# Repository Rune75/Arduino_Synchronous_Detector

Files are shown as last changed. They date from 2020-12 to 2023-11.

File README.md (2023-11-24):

# Arduino Synchronous Detector

This code demostrates a low frequency lockin amplifier or synchronous ligth detector inplementation using only a Arduino board and 2 additional modules: 
  1. The OPT101 amplified vissible light photodiode 
  2. A laser pointer 
  
The syncronous detector components are all realised in software 
using the Atmega328p builtin ADC as frontend and one GPIO for driving the laserdiode.

## Whys and hows
The idea behind a synchronous detector or lockin amplifier is best described trough an example. So lets asume we want to detect a moving target at some  distance. To be able to do this one could for example shine some ligth on the target and look for changes in the reflected light. If setting up this experiment with a light source and a photosensor we will soon discover that the reflected light variation we are trying to measure is not distingusable from variations in the ambient light level as shown in the top figure below. If we instead modulate our signal source with some frequency and lock our detector to the same frequency and phase we have what is called a synchronous detector. 

As shown below the synchronous demodulation process cancels out ambient noise and we are left with the signal of interest only.

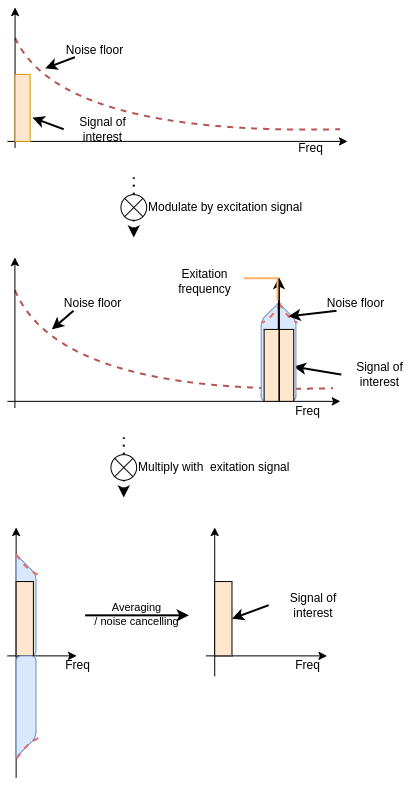
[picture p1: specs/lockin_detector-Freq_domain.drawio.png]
Frequncy domain


Thie noise cancelation part is a bit hard to grasp in the frequncy domain, but if we instead consider that the modulated source is realy just swithing on an off the light source at a constant frequency, and thus on the receiver side the same bacground noise will be present in both halfperiodes of the signal, both when the ligth source is on and when it is off. The demodulator is just a multiplicator that multiplies the signal with a square waveform with amplitude +1 to -1. at the same frequencuy and phase as the source modulation. The +- multiplication basicaly flips the sign on the noise in each halfperiode so the noise average over time from the demodulator is close to zero. This process is shown in the following figure.

### Basic principle
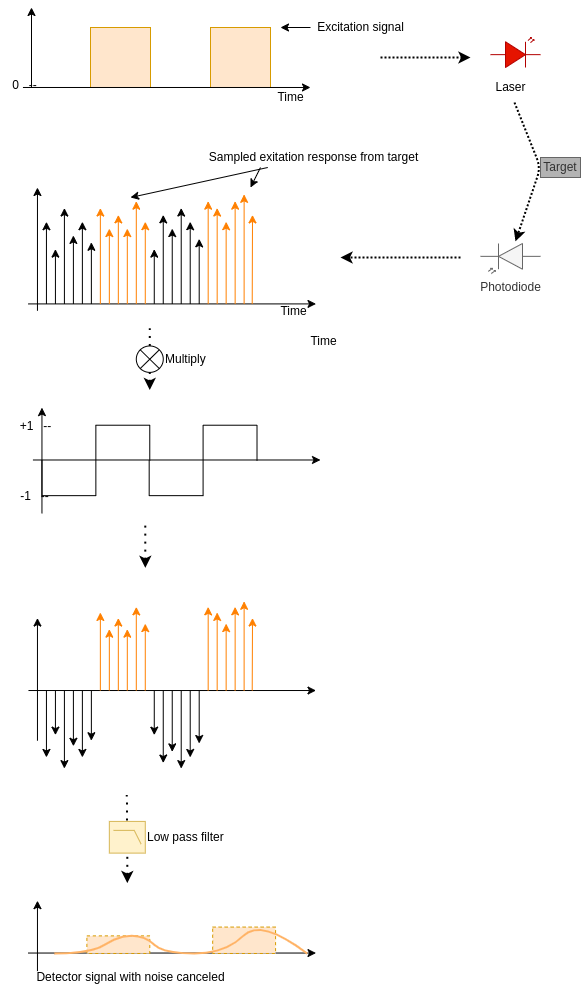
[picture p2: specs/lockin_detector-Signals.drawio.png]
Basic principle


### Analog implementation
The analog implenetation of a locking amplifier is shown below. These devices are built up around a oscilator and a RF mixer where the oscilator is source for both the exitation and the demodulator, this way it is always in phase lock.
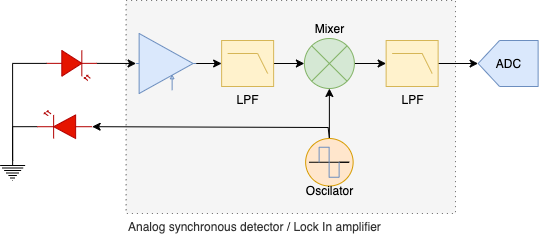
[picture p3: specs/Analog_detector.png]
Analog Synchronous detector


### Full microcontroller inplementation with Atmega328p
Understanding that a RF mixer is realy just a multiplicator we see that we can easily implement this whole circut in a microcontroller as shown below. 
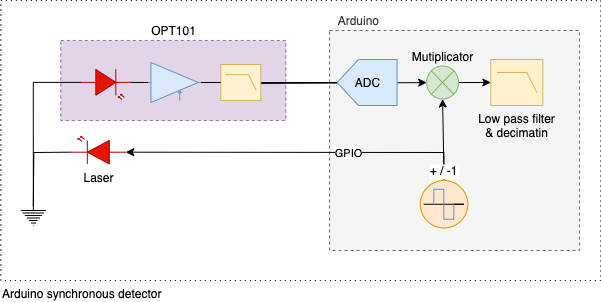
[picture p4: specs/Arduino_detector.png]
Arduino Synchronous detector


### Expanded view of actual implementation
By filtering the reflected signal while under exitation and the reflected signal when exitation is off in two separate arrays we are able to also measure and log the backround ligth level.
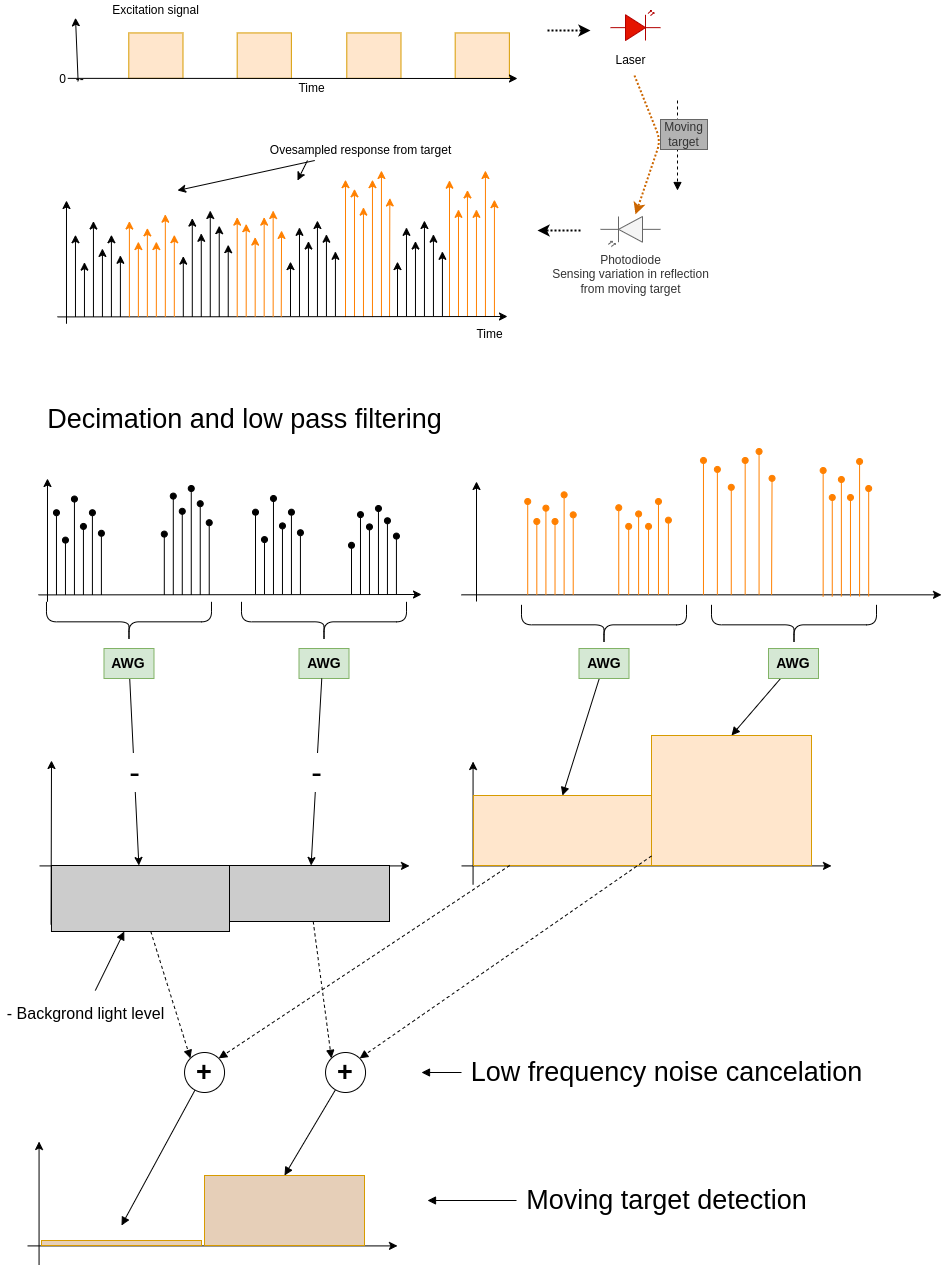
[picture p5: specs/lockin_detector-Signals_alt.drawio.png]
Signals_alt


###  Sampling and signal bandwith (work in progress)
ADC raw samplerate with prescaler set to 16 in free running mode is 16 MHz/(16*13) ≈ 77kHz. estimated > 8 bit resoluition. 
(LSB is a bit unstable because of the high samplerate).
The resulution is then increased by 6 bit trough downsampling by 4^6 = 4096 giving us a downsampled samplerate of 77k / 4096 = 18.79Hz
The exitation pulse length is set to 16 samples and 50% dudty cycle so the Exitation pulse rate is 77kHz/(2*16) = ~2404Hz.
The bandwith of the opt101 sensor is 14KHz so 2.4kHz exitation frequency is wel within this band.

Ewerything is divided down from and synchronous to the ADC raw samplerate.

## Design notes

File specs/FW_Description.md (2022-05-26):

FW Description

Arduino Synchronous detector

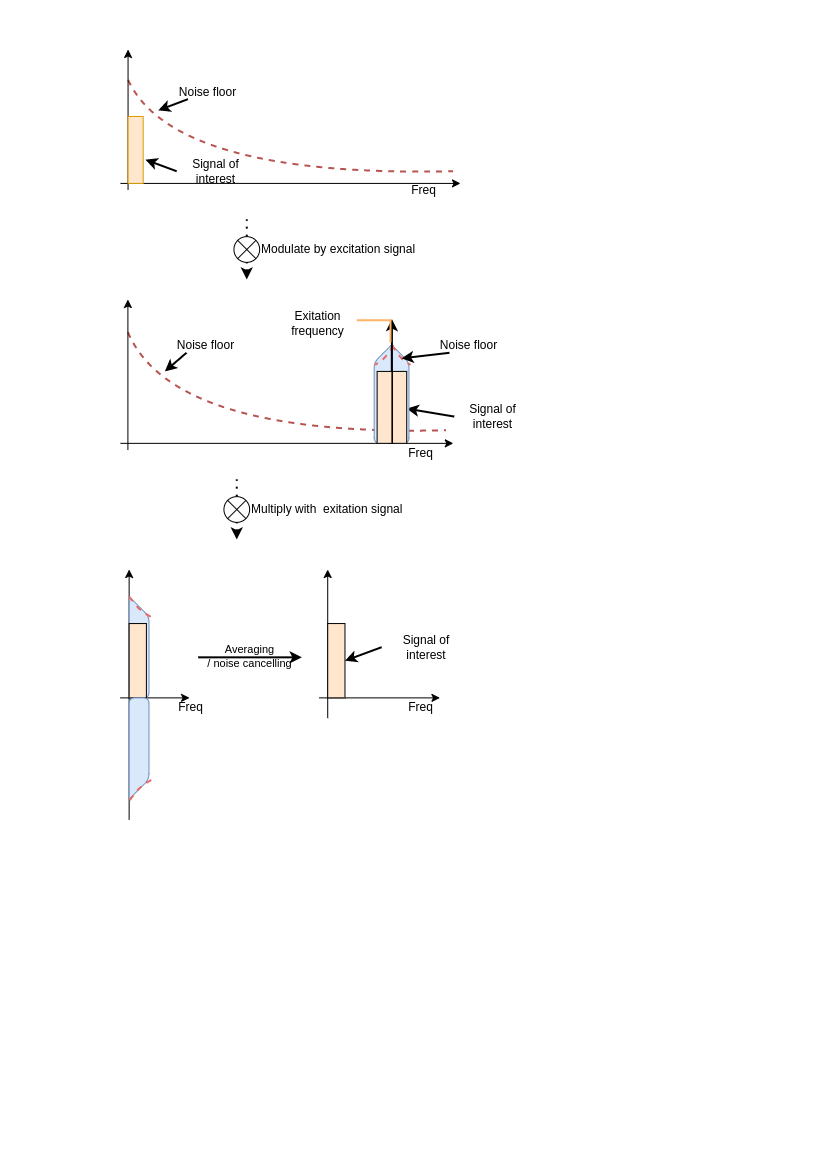
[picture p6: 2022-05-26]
specs/lockin_detector-Freq domain.drawio.png

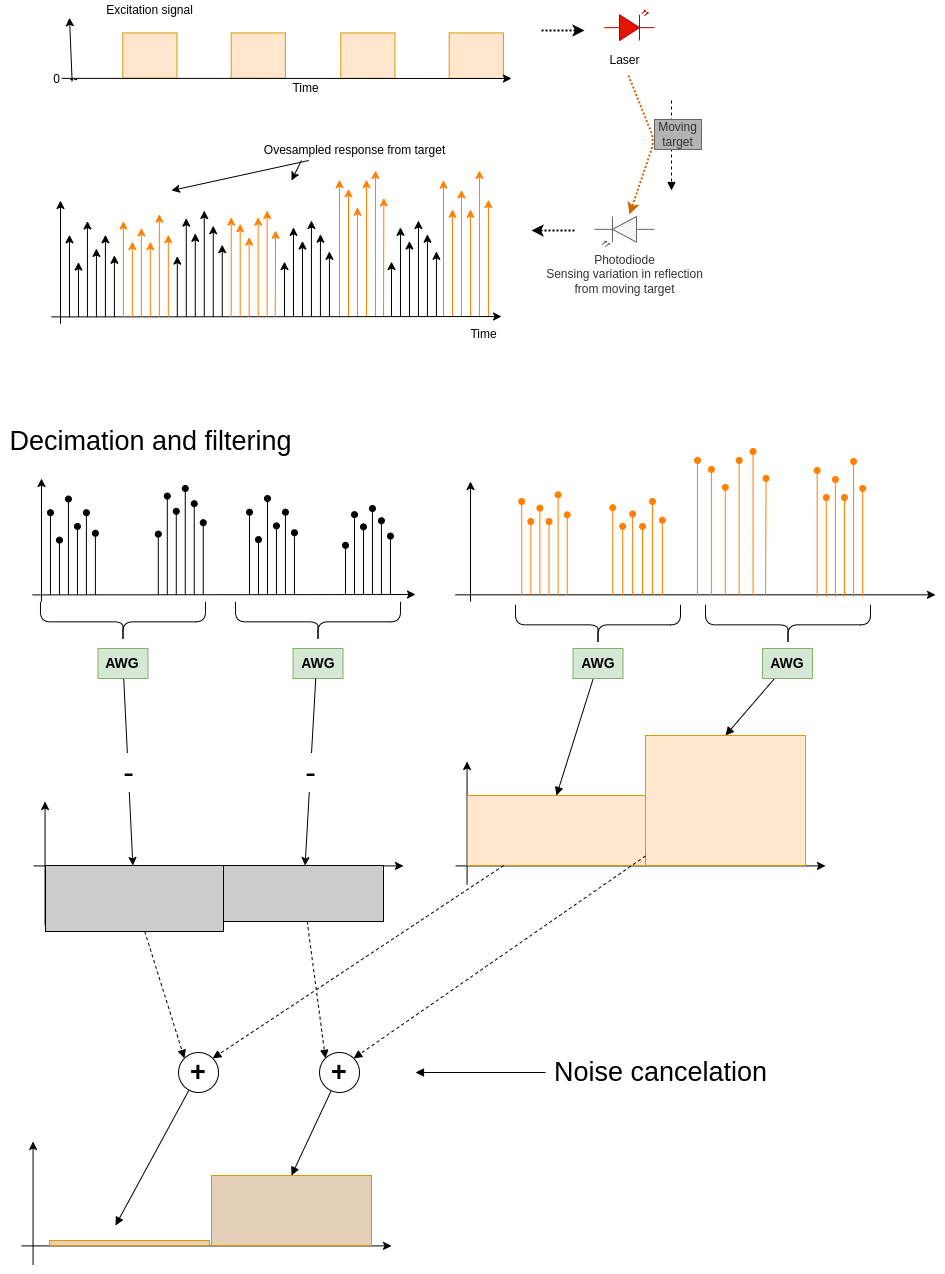
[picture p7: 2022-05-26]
specs/lockin_detector-Signals.png

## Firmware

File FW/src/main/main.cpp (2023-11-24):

/*
 * This code demostrates a low frequency lockin amplifier or synchronous ligth 
 * detector inplementation using only a Arduino board and 2 additional modules:
 *   1. Atmega328p Arduino board w synchronous detector inplementation in code
 *   2. The OPT101 amplified vissible ligth photodiode 
 *   3. A laser pointer 
 * 
 * The syncronous detector components ar all realised in software 
 * using the Atmega328p builtin ADC as frontend.
 * 
 * Basic spec
 * ----------
 * ADC raw samplerate is 78.6kHz with estimated > 8 bit resoluition. 
 *    LSB is a bit unstable becuse of the high samplerate but is giving better relative 
 *    resolution wit this compared to lovering the samplerate and decimation ration
 * ADC resolution is >14 bit after oversampoling and decimation
 * Laser modulation or exitation frequency 12.8kHz, and so also the LO frequency of the sychronous detector.
 * After decimation the output samplerate from the detector is 12.8 / 4^6 = 3.125 kS/s
 * Ewerything is divided down and synchronous to the ADC raw samplerate clock.
 * 
 * Copyright (c) 2020 Rune Bekkevold
 * Released under the terms of the MIT license:
 * https://opensource.org/licenses/MIT
 * 
 */

#include <Arduino.h>

#define DEBUGPRINT 1;
#ifdef DEBUGPRINT
    #define DEBUG_PRINT(x)    Serial.print (x)
    #define DEBUG_PRINTDEC(x) Serial.print (x, DEC)
    #define DEBUG_PRINTLN(x)  Serial.println (x)
    #define DBG_PRINTF(y,x)  Serial.print(y); Serial.println(x);
#else
    #define DEBUG_PRINT(x)
    #define DEBUG_PRINTDEC(x)
    #define DEBUG_PRINTLN(x) 
    #define DBG_PRINTF(y,x)
#endif

#define DEBUGPINS 1;
#ifdef DEBUGPINS
    #define DEBUG_PIN_TOGGLE(x)     PORTD ^= _BV(x);    // Toggle pin
    #define DEBUG_PIN_SET(x)        PORTD |= _BV(x);    // Set pin high
    #define DEBUG_PIN_CLR(x)        PORTD &= ~(_BV(x)); // Set pin low
#else
    #define DEBUG_PIN_TOGGLE(x)
    #define DEBUG_PIN_SET(x)
    #define DEBUG_PIN_CLR(x)
#endif


// -- Input and output pins -------------------- 
const uint8_t sensorPin = 0;        // Analog input connected to the photo sensor
const uint8_t ExPin = 2;            // Set D2 pin as Laser exitation output

// -- Debugg output pins ------------------------
const uint8_t sampleIndicator = 3;  // Indicator pin for sample rate
const uint8_t serialIndicator = 4;  // Indicator pin for serial write
const uint8_t ADCisrIndicator = 5;  // Indicator pin for ISR(ADC_vect) duration


// ADC resolition ioncreased by oversampling an decimation
const uint8_t ADCincreasedRes = 6;                                  // For adding 6 extra bits ADC resolution
const uint16_t decimationFactor = (int)pow(4, ADCincreasedRes);     // decimate oversampled data by 4^increasedRes

const uint8_t exPulseLen = 16;      // Exitation pulse length set in number of ADC samples
volatile bool ligthReadingReady;    // Light reading ready indicator, provided by the ADC interrupt service routine.

struct detectorRes {                // Results struct 
    uint32_t exitationLvl;
    int32_t backgroundLvl;
    int32_t differenceLvl;
};
volatile detectorRes sampleSum;     // Results object


//-- ADC interrupt service routine -----------------------------------------
//-- Called each time a conversion result is available.
ISR(ADC_vect)
{
    DEBUG_PIN_SET(ADCisrIndicator); //Debug pin set for indicating that a ADC conversion result is ready, and we entered the interupt routine

    int32_t sample = ADC;    // Copy the sample from the ADC.
    
    // Declare interupt function specific static variables
    static uint16_t decimationCounter;      // Keeping track of Decimation length
    static uint8_t exitationCounter;        // Keeping track of number of passed exitation pulses
    static int32_t backgroundLvlAcc;        // Cumulative sum of Background ligth level readings
    static bool ExitationOn;                // Indicates state of exitation output
    static int32_t exitationLvlAcc;         // Cumulative sum of exited light level

    decimationCounter++;
    exitationCounter++;
    
    if (!ExitationOn) {                 // If Laser exitation is off
        backgroundLvlAcc += sample;     // Acumulate ambient ligth level
    } else {
        exitationLvlAcc += sample;      // else acumulate exited ligth level
    }

    //-- store acumulators when decimationFactor number of samples is reached
    //-- Occurs when we have enough summed samples for one output sample
    if (decimationCounter == decimationFactor) 
    { 
        DEBUG_PIN_SET(sampleIndicator);             // Debug pin set
        sampleSum.exitationLvl = exitationLvlAcc;   // Output auccumulated  exited light level readings
        sampleSum.backgroundLvl = backgroundLvlAcc; // Output auccumulated  background light level readings
        backgroundLvlAcc = 0;                       // reset ambient Acc to 0 
        exitationLvlAcc = 0;                        // reset sample accumulator to previous sample;

        decimationCounter = 0;                      // Reset decimation counter
        exitationCounter = exPulseLen;              // Reset exitation counter, syncronizes exitation with sample reading

        ligthReadingReady = true;                   // Tell the world that accummulators are ready for division
    }

    // Toggle exitation every exPulseLen samples
    if (exitationCounter == exPulseLen) {
        if (!ExitationOn) {
            PORTD = PORTD | 0b00000100; // Set exitation pin D2 high
            ExitationOn = true;
        }
        else {
            PORTD = PORTD & 0b11111011; // Set exitation pin D2 low
            ExitationOn = false;
        }
        exitationCounter = 0;
    }    
    DEBUG_PIN_TOGGLE(ADCisrIndicator);  // Debug pin Toggle to indicate interupt routine has finished
}


//-- 
detectorRes sampleACCdownConvSimple()
{
    detectorRes res;
    res.exitationLvl = (uint32_t)(sampleSum.exitationLvl / pow(2, ADCincreasedRes-1)); // ##- wonder if it should not be -1 here ???????? 

    // get ambient light level
    res.backgroundLvl = (int32_t)(sampleSum.backgroundLvl / pow(2, ADCincreasedRes-1));

    res.differenceLvl = (int32_t) (res.exitationLvl - res.backgroundLvl);
    return res;
}

detectorRes sampleACCdownConv()
{
    detectorRes results;
    if (sampleSum.exitationLvl > 0)
    {   // Accumulator value is positive. cast acc to uint and rigthshift with virtual resolution invrease
        results.exitationLvl = (int32_t)(((uint32_t)sampleSum.exitationLvl) >> ADCincreasedRes);
    }
    else
    { // Accumulator value is negative, flip sign and cast acc to unsigned before right shift
        results.exitationLvl = -(int32_t)(((uint32_t)-sampleSum.exitationLvl) >> ADCincreasedRes);
    }

    // get ambient light level
    results.backgroundLvl = (sampleSum.backgroundLvl >> (ADCincreasedRes - 1)); // the ambient level measurement is only half the number of samples so we shift one bit less
    return results;
}

void setup()
{
    // Configure the ADC in "free running mode".
    ADMUX = _BV(REFS0)    // ref = AVCC
            | sensorPin;  // input channel
    ADCSRB = 0;           // free running mode
    ADCSRA = _BV(ADEN)    // enable
             | _BV(ADSC)  // start conversion
             | _BV(ADATE) // auto trigger enable
             | _BV(ADIF)  // clear interrupt flag
             | _BV(ADIE)  // interrupt enable
             | 4;         //4  prescale 16 //5; // prescaler 32. 7;  // prescaler = 128.

    // Configure the serial port.
    Serial.begin(115200);

    // configure Exitation pin mode and initial state;
    pinMode(ExPin, OUTPUT);
    digitalWrite(ExPin, HIGH);

    // Configure the other pins and initial states
    pinMode(sampleIndicator, OUTPUT);
    digitalWrite(sampleIndicator, HIGH);

    pinMode(serialIndicator, OUTPUT);
    digitalWrite(serialIndicator, HIGH);

    pinMode(ADCisrIndicator, OUTPUT);
    digitalWrite(ADCisrIndicator, HIGH);
}

void loop()
{
    // Wait for interupt routine to finsh, saying a reading a reading is available.
    while (!ligthReadingReady) /* wait for interupt */
        ;
    ligthReadingReady = false;
    
    // Get a copy of the detecor result
    //detectorRes detectorReadings = sampleACCdownConv();
    detectorRes detectorReadings = sampleACCdownConvSimple();
    DEBUG_PIN_TOGGLE(sampleIndicator);

    digitalWrite(serialIndicator, HIGH);

    //- print out results for Teleplot---
    DBG_PRINTF(">BackGround:", detectorReadings.backgroundLvl);     // Print Background level
    DBG_PRINTF(">ExitedLvl:", detectorReadings.exitationLvl);       // Primt Reflected level + ambient
    DBG_PRINTF(">Result:", detectorReadings.differenceLvl);

    digitalWrite(serialIndicator, LOW);

}

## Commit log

2020-12-11 Update main.cpp
    Fixed some comments and found a bug in the sample code counter so made the code break compilation until I get that fixed.
2021-12-09 debug print
2023-11-20 added Kicad project
    [Arduino_Synchronous_Detector.csv, Arduino_Synchronous_Detector.kicad_pcb, Arduino_Synchronous_Detector.kicad_sch, Arduino_Synchronous_Detector_12V.kicad_sch]
2023-11-24 Cleaned up comments and changed output print to teleplot
